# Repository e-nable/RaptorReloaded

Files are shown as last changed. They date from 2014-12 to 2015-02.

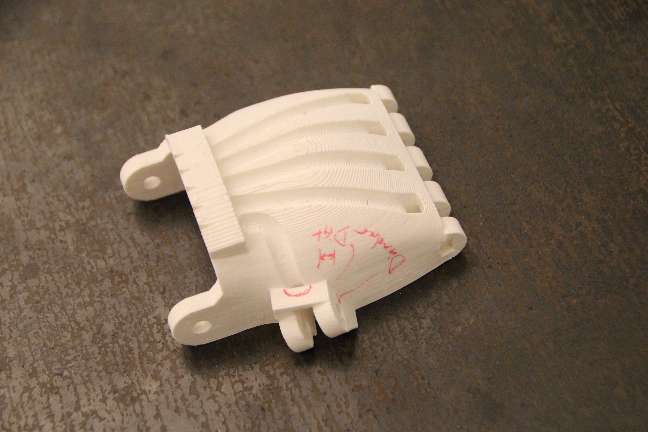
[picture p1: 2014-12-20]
Assembly Images/IMG_4811.JPG

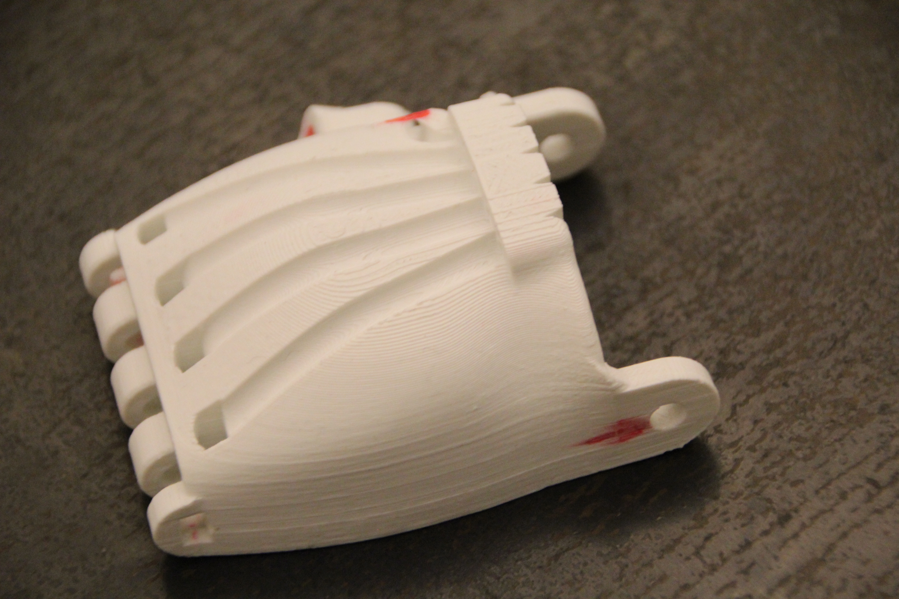
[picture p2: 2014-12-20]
Assembly Images/IMG_4816.JPG

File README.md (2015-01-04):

RaptorReloaded
==============

The Raptor Reloaded is an assistive device synthesized from designs and feedback from the e-NABLE community.  The philosophy and motivation behind this design is to lower the barrier to contribution and collaboration.  By making source files available in a variety of established and standard formats, we are making it easier for community members to test ideas using the modular and well-documented Raptor Reloaded design.  

The files in this repo are the static release files and will be updated periodically to incorporate improvements generated by the community.

## 12-20-14 Commit by AB

- added STLs oriented for use ing Hand-o-matic and plaed for printing
- aded PDF schematics of individual parts
- added images of assembly and comparisons between Raptor Reloaded, the Raptor Original, and the Cyborg Beast

## 1-4-15 Commit by AB

- fixed fit problem with finger pin (raptor_2.0_finger_pin.stl)
- updated all instances of the finger pin (HOM, Print, plates, STLs for printing.zip)

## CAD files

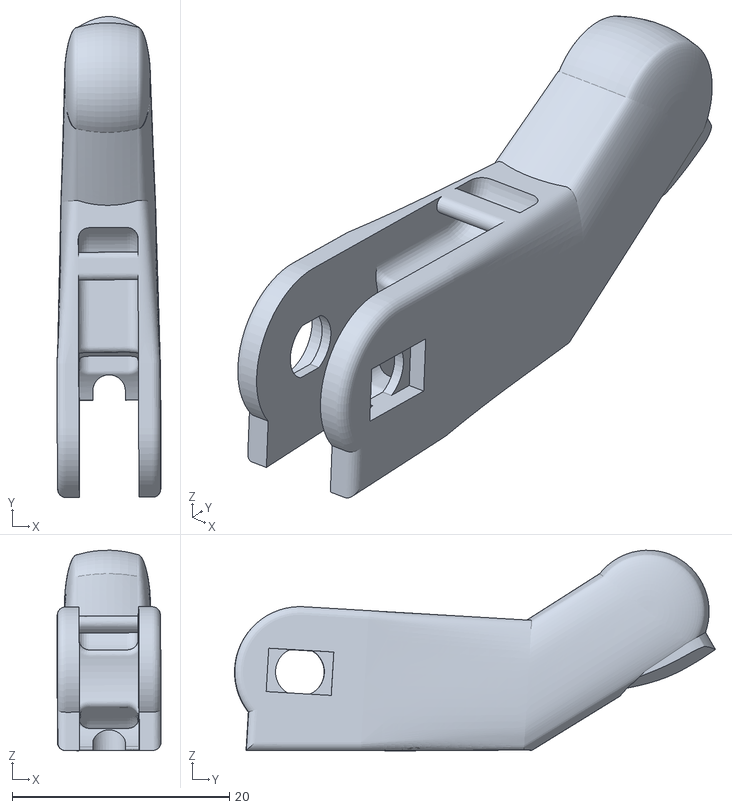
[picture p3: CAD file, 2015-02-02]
STLs/HOM/raptor_reloaded_fingertip_with_nail.stl
9.58 x 44.3 x 18.5

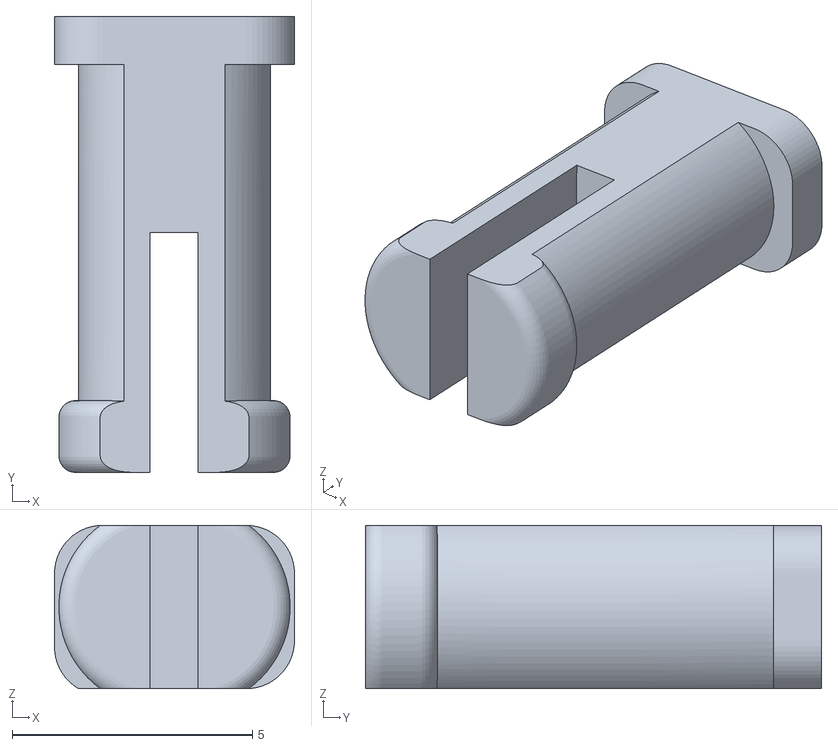
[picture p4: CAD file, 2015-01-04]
STLs/HOM/raptor_2.0_finger_pin.stl
5.00 x 9.50 x 3.40

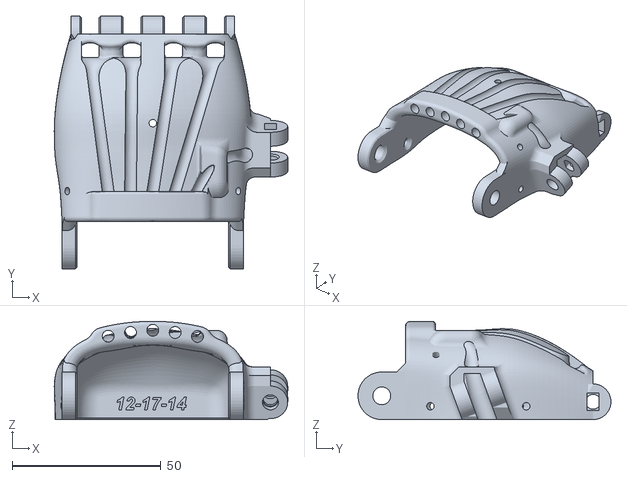
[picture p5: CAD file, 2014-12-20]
STLs/HOM/raptor_reloaded_left_palm.stl
78.4 x 85.0 x 33.0

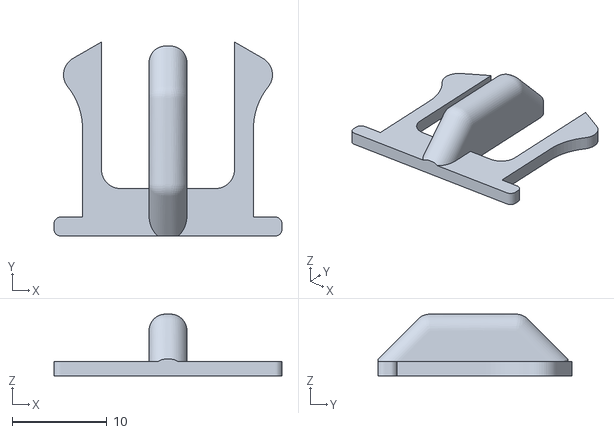
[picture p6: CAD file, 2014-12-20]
STLs/Print/raptor_reloaded_retention_clip.stl
24.0 x 20.4 x 6.50

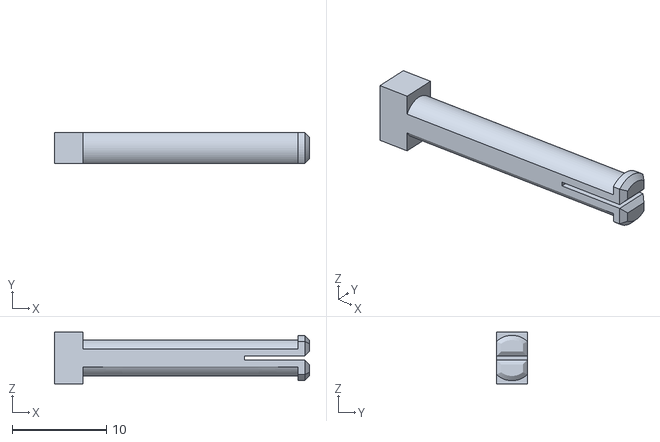
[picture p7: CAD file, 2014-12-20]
STLs/HOM/raptor_reloaded_knuckle_pin.stl
27.0 x 3.30 x 5.50

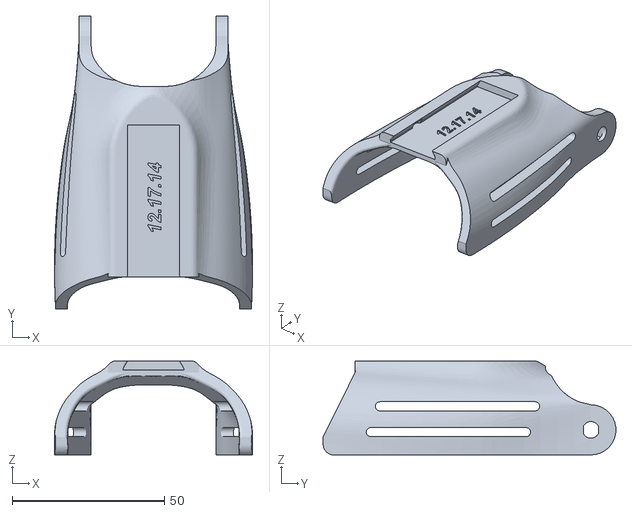
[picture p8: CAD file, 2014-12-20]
STLs/Print/raptor_reloaded_gauntlet.stl
65.1 x 96.2 x 30.9

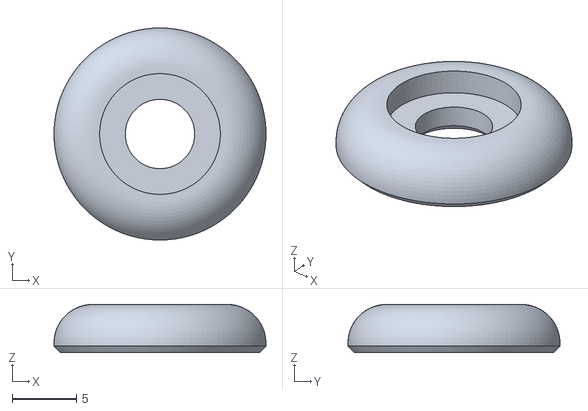
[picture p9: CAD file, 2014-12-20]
STLs/Print/raptor_reloaded_wrist_pin_cap.stl
16.5 x 16.5 x 3.75

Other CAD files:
STLs/Print/raptor_reloaded_fingertip_with_nail.stl
STLs/HOM/raptor_2.0_fingertip.stl
STLs/Print/raptor_2.0_fingertip.stl
STLs/HOM/raptor_reloaded_gauntlet.stl
STLs/Print/raptor_reloaded_knuckle_pin.stl
STLs/HOM/raptor_reloaded_gauntlet_support.stl
STLs/HOM/raptor_reloaded_left_palm_support.stl
STLs/HOM/raptor_reloaded_retention_clip.stl
STLs/HOM/raptor_reloaded_right_palm.stl
STLs/HOM/raptor_reloaded_right_palm_support.stl
STLs/HOM/raptor_reloaded_wrist_pin_cap.stl
STLs/Print/raptor_reloaded_gauntlet_supported.stl
STLs/Print/raptor_reloaded_left_palm.stl
STLs/Print/raptor_reloaded_right_palm.stl

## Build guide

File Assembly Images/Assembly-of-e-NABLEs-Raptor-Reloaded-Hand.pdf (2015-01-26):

http://www.instructables.com/id/Assembly-of-e-NABLEs-Raptor-Reloaded-Hand/

Food (http://www.instructables.com/tag/type-id/category-food/) Living (http://www.instructables.com/tag/type-id/category-living/) Outside (http://www.instructables.com/tag/type-id/category-outside/) | Play (http://www.instructables.com/tag/type-id/category-play/) | Technology (http://www.instructables.com/tag/type-id/category-technology/) Workshop (http://www.instructables.com/tag/type-id/category-workshop/)

# Assembly of e-NABLE's Raptor Reloaded Hand

by andreasbastian (http://www.instructables.com/member/andreasbastian/?utm_source=pdf&utm_campaign=title) on January 15, 2015

Table of Contents

Author:andreasbastian Andreas Bastian (http://andreasbastian.com)
Engineer and artist working with 3D printing, laser cutting, and clay.

## Intro: Assembly of e-NABLE's Raptor Reloaded Hand

The Raptor Reloaded is an updated release of the original that incorporates feedback from the e-NABLE community (https://plus.google.com/communities/102497715636887179986/) and has CAD design source files available in STEP, IGES, IPT, and F3D formats.

Updates in the 12-17-14 release include:
Improved print-ability due to custom modeled supports
Cyborg Beast compatible sizing
Improved dovetail geometry
New tensioner retention clip
Easier to use tensioner pins
Low profile elastics with two tie-off options
More access to elastic and flexsor routing channels Debossed versioning information on palm and gauntlet Slimmer, more anthropomorhpic fingers
Narrower knuckle block
More intuitive assembly (new one-way proximals)
Thorough documentation and modular design
Source files in native Fusion 360 format, also STEP and IGES
Additional velcro-mounting options as well as traditional velcro loop and leather options Re-oriented snap-pin head recesses to improve printability
Knuckle pins are now removable, making the hand easy to repair and upgrade Strengthened tie-bars on finger tips

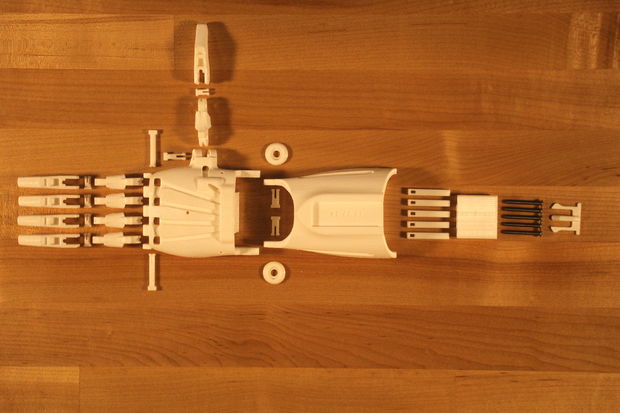
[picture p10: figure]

Image Notes
1. Palm (left)

Image Notes
1. Gauntlet

Image Notes
1. Proximal phalange

Image Notes
1. Fingertip

Image Notes
1. Finger snap pin

Image Notes
1. Knuckle snap pin

Image Notes
1. Thumb snap pin

Image Notes
1. Tensioner retention clip

Image Notes
1. Tensioner block

Image Notes
1. Tensioner pin

Image Notes
1. Wrist snap pin

Image Notes
1. Wrist snap pin cap

## Step 1: Size and Print the Parts, Secure Hardware

Download the latest Raptor Reloaded parts form Thingiverse. (http://www.thingiverse.com/thing:596966) The files are ready to print as is and do not require additional support material as custom removable support structures have already been modeled into the palm and gauntlet files. If you do wish to print without the included support, files without support are also available on the Thingiverse page.

There are two main options for sizing the Raptor Reloaded:

Linear Scaling (easy)

The main measurement used in sizing the Raptor Reloaded is the width of the recipient's complete hand at the knuckles. At 100% scale, the palm of the Raptor Reloaded measures 55mm at its widest point. To get the appropriate linear scaling factor for scaling the STLs, add 5mm (to account for the thickness of padding in the printed palm) to the width of the recipient's complete hand at its widest point. Divide this number by 55 to get the scaling factor for the STLs. For example, if the palm is 65mm wide, then 65 + 5 = 70, and 70 / 55 = 1.27, so the scaling multiplier would be 1.27 or 127%. Make sure to apply the scaling factor to all of the parts to ensure that they fit together. At higher scales, the clearances between the moving parts of the hand will grow, so glue or other modifications may be necessary to ensure that all the pieces stay secured to each other.

Parametric (more involved):

Because radial and lateral clearances for motion assemblies are absolute, linear scaling can cause problems at large scales. For those with some CAD experience, the native Fusion 360 source files as well as STEP and IGES files are available here. (http://a360.co/1uV2X0G) Detailed technical drawings can be found on the github. (https://github.com/e-nable/RaptorReloaded/tree/master/Drawings) For an introduction to modeling in Fusion 360, see the Getting Started in Fusion 360 (http://enablingthefuture.org/resources/getting-started-in-fusion-360/) page on enablingthefuture.org.

Recommended Printing Settings:
PLA (or ABS, PET, Nylon)
0.2mm layers
2 shells
35% infill
Active cooling fan on

Additional Materials:

The Raptor Reloaded requires some additional hardware to assemble, most of which can be sourced from the Hardware Sources (http://enablingthefuture.org/resources/hardware-sources/) page on the e-NABLE website. 4ft Velcro, double-sided (2” wide) (http://www.amazon.com/Velcro-Nylon-Length-Width-Black/dp/B003L1W4DQ/ref=pd_sim_op_5)

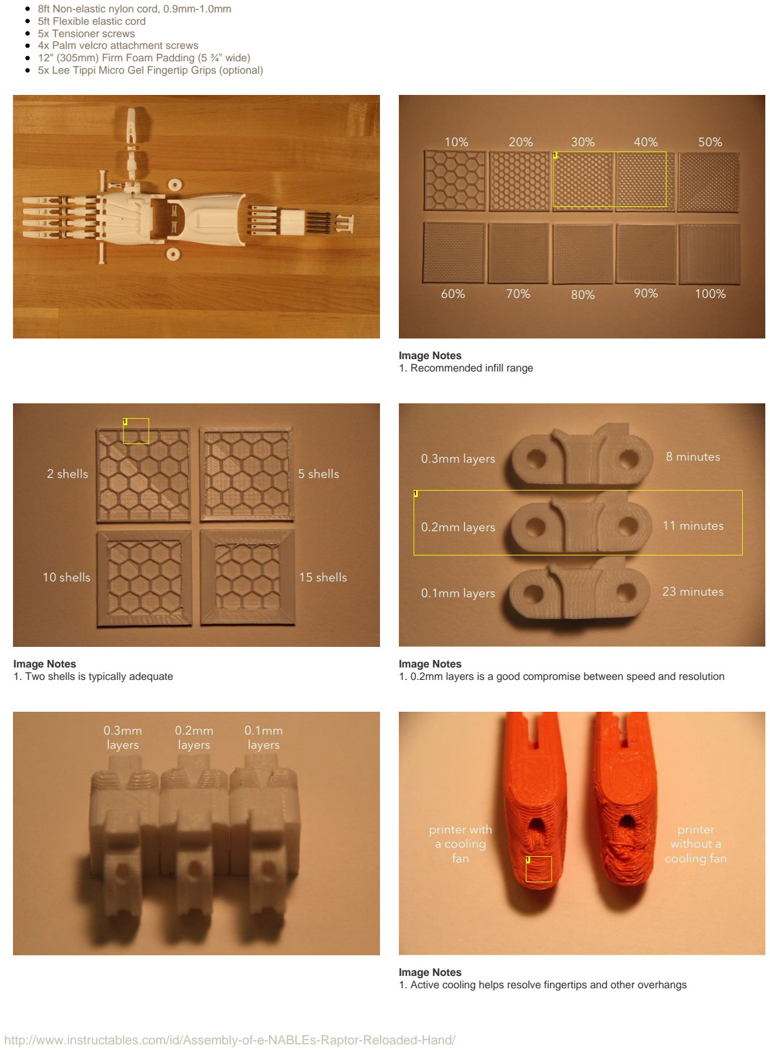
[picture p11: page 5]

8ft Non-elastic nylon cord, 0.9mm-1.0mm (http://www.amazon.com/gp/product/B009661Y72/) 5ft Flexible elastic cord (http://www.amazon.com/gp/product/B0047BIRUS/)
5x Tensioner screws (https://www.boltdepot.com/Socket_button_head_Stainless_steel_18-8.aspx)
4x Palm velcro attachment screws (https://www.boltdepot.com/Socket_flat_head_Stainless_steel_18-8.aspx)
12" (305mm) Firm Foam Padding (5 ¾” wide) (http://www.pattersonmedical.com/app.aspx?cmd=getProductDetail&key=070_921018416) 5x Lee Tippi Micro Gel Fingertip Grips (optional) (http://www.amazon.com/s/ref=nb_sb_noss_2?url=search-alias%3Daps&field-keywords=gel+tippi)

Image Notes
1. Recommended infill range

Image Notes
1. Two shells is typically adequate

Image Notes
1. 0.2mm layers is a good compromise between speed and resolution

Image Notes
1. Active cooling helps resolve fingertips and other overhangs

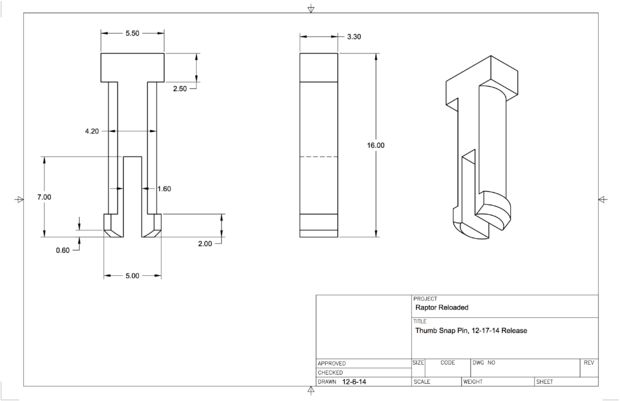
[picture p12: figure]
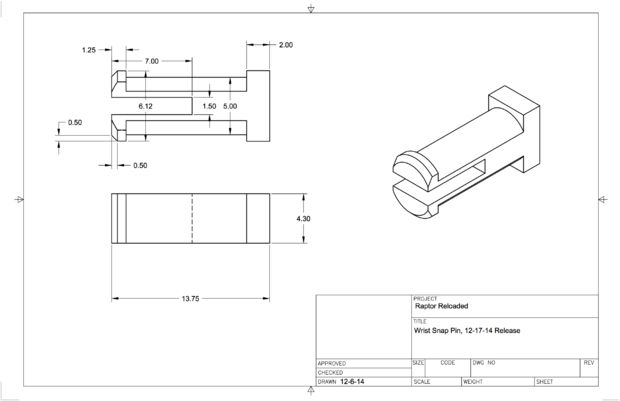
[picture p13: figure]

## Step 2: Assemble the Palm and Fingers

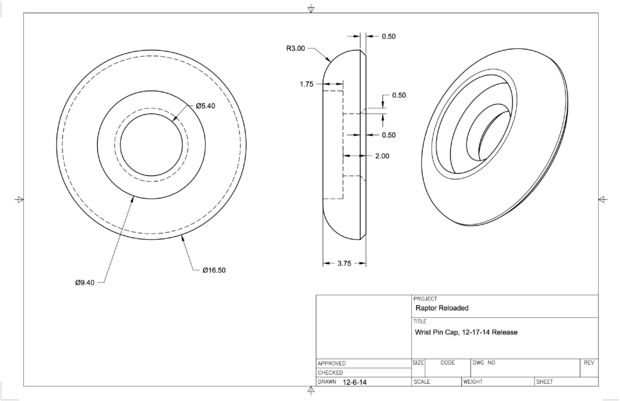
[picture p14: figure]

Start by removing the support structure, which can be done by inserting any edged tool in between the palm and the support structure and twisting. Next, check the fingertips for any defects. Small pieces of filament sometimes droop in the rectangular recess for the snap pin head-- be sure to remove these to ensure the snap pin seats well.

Assemble the fingers by inserting the proximal phalange into the matching recess in the fingertip, making sure the raised hard stop (the "square" region on top of one side of the proximal phalange) is facing away from the fingertip and the two small ridges on the top of the proximal meet the matching "wings" of the fingertip. Insert the snap pin and press until the rectangular head is seated in it's recess and the other end of the pin is flush with the sides of the fingertip. Repeat for the remaining four fingers. Attach the one finger to the thumb knuckle on the palm using the thumb pin and attach the other four fingers in the knuckles using the two knuckle pins. It is often helpful to get the knuckle pin started and then push its head using a table. If at a later point you need to remove or replace fingers, the knuckle pins can be backed out by pressing on their tips using the slot in between the bases of the middle and ring finger.

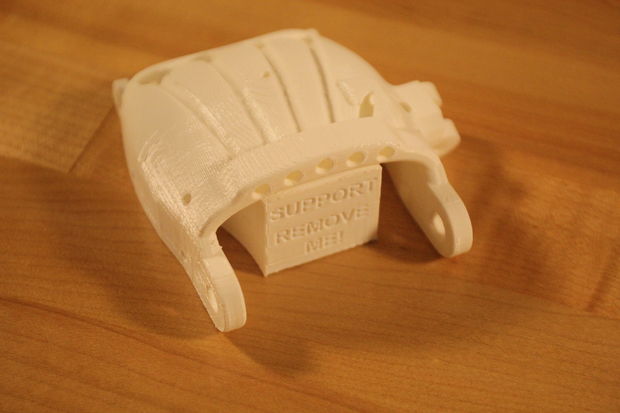
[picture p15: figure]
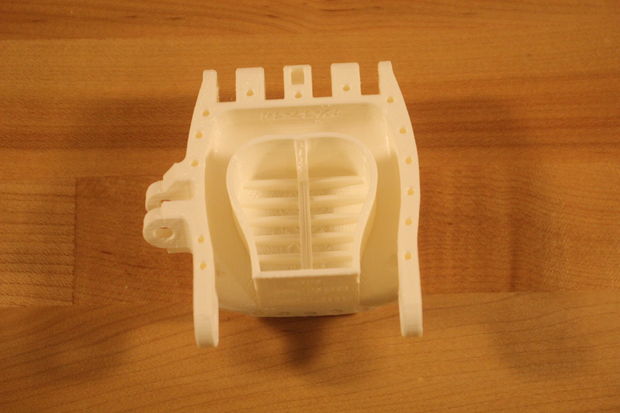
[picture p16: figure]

Image Notes
1. Any tool with an edge will work for removing the support structure.

Image Notes
1. Sometimes the fingertips print with a small defect here.

Image Notes
1. It can be removed with a blade or tweezers.

Image Notes
1. Fingertip

Image Notes
1. Thumb pin

Image Notes
1. The knuckle snap pins can be removed by pushing on them from this slot.

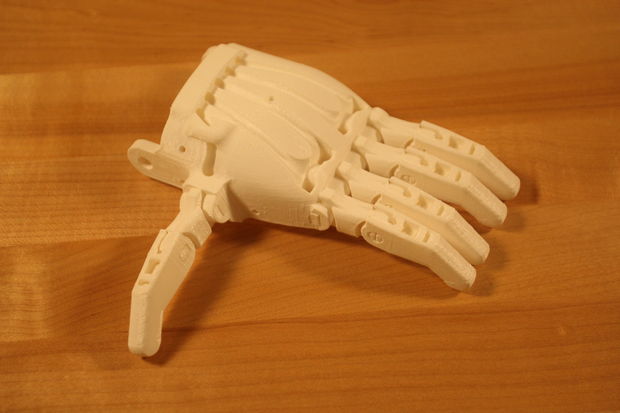
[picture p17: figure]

## Step 3: Install the Elastics in the Fingers

Check the Hardware Sources (http://enablingthefuture.org/resources/hardware-sources/) page on the e-NABLE website for vetted elastics options. I used 1.0mm black Beadlon elastic fabric cord (http://beadalon%20fabric%20elastic/) from Amazon. Cut five lengths each a little longer than two finger lengths. I like to use tweezers to navigate the tight spaces where the elastics are tied. The goal of the elastics is to just counter to force of gravity on the fingers and to hold them gently open. This opening force is calibrated when tying the second end of the elastic cord to the back of the palm. The fingers should snap up after being pressed down, but should not require significant force to close.

Sarting with the thumb, thread one end of a length of elastic cord under the bar on the back of the thumb tip until there is a little over an inch (30-35mm) of cord on the other side of the bar. Tie a clinch knot by twisting the free end around the longer side 2-4 times, then thread the free end through the loop at the base of the twist and through again the resulting loop:

After threading the elastic cord through the proximal and up through the cable guide, use the clinch (or two half hitch) knot to secure the end of the elastic cord to the cable guard as shown in the pictures. The goal is to use this knot to set the tension on the thumb, so tie it carefully after getting the appropriate tension.

For the remaining four fingers, I like to use the clinch knot on the finger tips and a two half hitch knot to secure the other end of each elastic to the rear cable guide on the palm. The two half hitch knot allows you to control the tension while tying the knot. See below:

Finally, I like to finish each elastic knot with super glue to ensure that it won't slip. Additional half hitchs can be used as well.

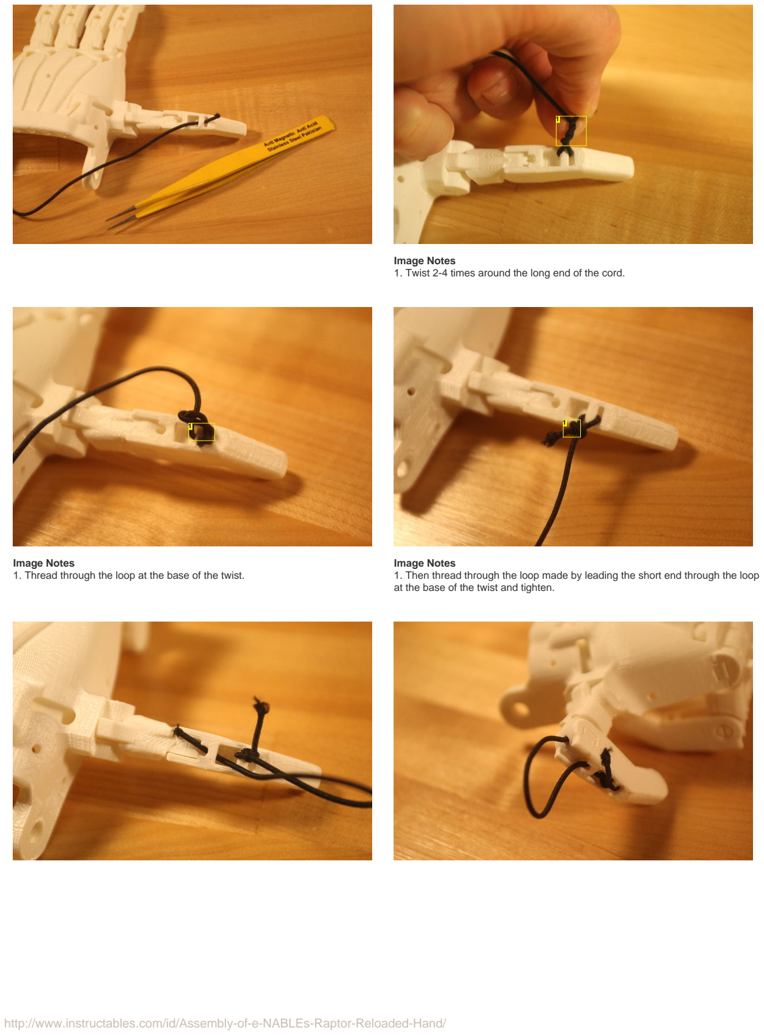
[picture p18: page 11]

Image Notes
1. Twist 2-4 times around the long end of the cord.

Image Notes
1. Thread through the loop at the base of the twist.

Image Notes
1. Then thread through the loop made by leading the short end through the loop at the base of the twist and tighten.

Image Notes
1. I used a clinch knot again, but a two half hitch would work just as well if not better.

Image Notes
1. Trim the knot tails.

Image Notes
1. A drop of superglue helps secure each knot.

Image Notes
1. One half hitch.

Image Notes
1. Adjust the tension using the single half hitch, then tie a second half hitch to lock it in.

Image Notes
1. Two half hitch knot keeps the cord from slipping.

Image Notes
1. Two half hitches.

## Step 4: Install the Flexsors in the Fingers

Again, check the Hardware Sources (http://enablingthefuture.org/resources/hardware-sources/) page on the e-NABLE website for other vetted sources of flexsor line. This braided nylon fishing line (http://www.amazon.com/gp/product/B009661Y72/) is the current recommended material for the flexsors. As with the elastic lines, I like to use a clinch knot to secure the flexsors to the finger tips.

Cut five lengths of nylon line, each as long as the ultimate length of the assembled hand (fingers plus palm plus gauntlet). This is a good way to make sure that you have enough line when working with different scales. Starting with the thumb, use a clinch knot to tie on e end of the flexsor line to the tie-bar. Then thread the line through the proximal and up through the proximal knuckle where the proximal phalange meets the palm. Be careful to ensure that the line doesn't get wrapped around the elastic cord for each finger. It should run parallel to it up over the top of the palm and out the back of the rear cable guide. Repeat this process for the other four fingers. After trimming the knot tails, I like to singe the tail to prevent fraying and then apply a drop of superglue to make sure the knot doesn't slip.

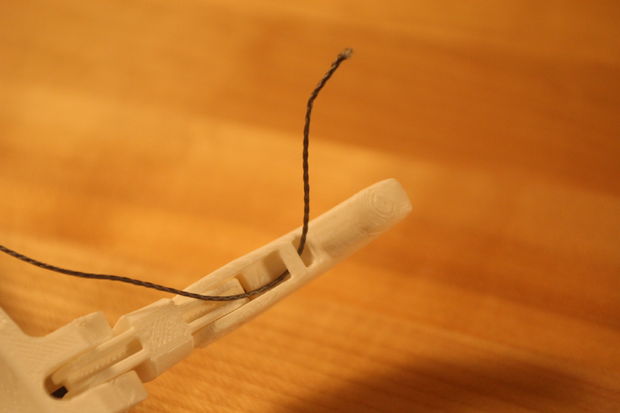
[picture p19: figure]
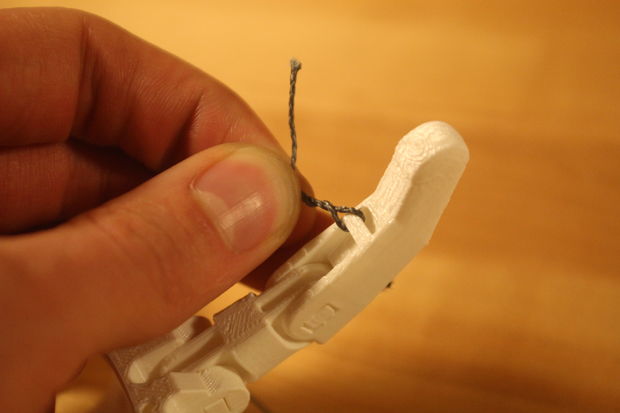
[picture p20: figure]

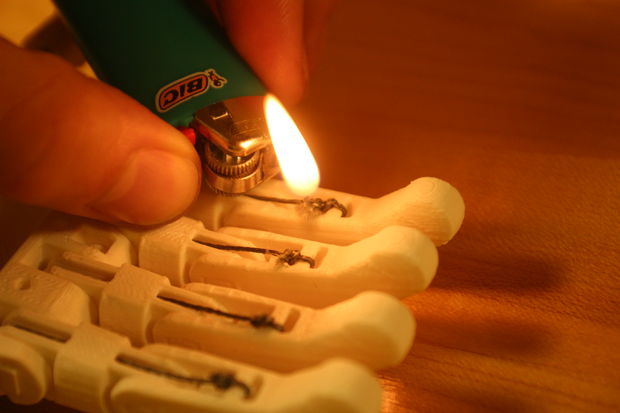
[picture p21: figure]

## Step 5: Attach the Palm to the Gauntlet

Using an edged tool, remove the gauntlet support structure and set it asides for use in the next step. Press the two wrist snap pins through the holes in the gauntlet, making sure they are aligned with the head recesses on the inner faces of the gauntlet. Once they have snapped through, back the tips back and slide the palm into position so that the wrist axis is aligned. Press the wrist pins through the palm's wrist holes. If necessary, the wrist can be bent back and the corner of a table can be used to apply pressure to the pins. Once the pins are properly seated, snap the pin caps over each pin to complete the wrist.

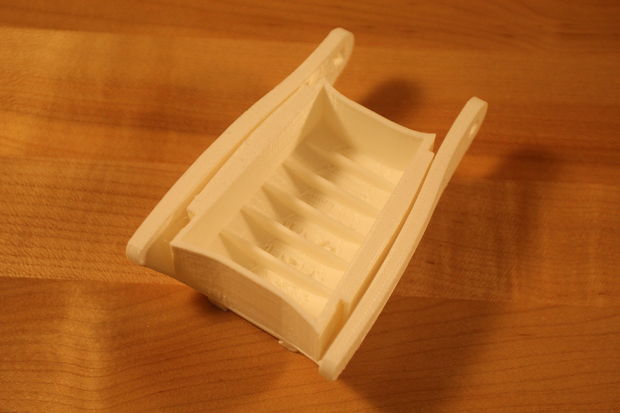
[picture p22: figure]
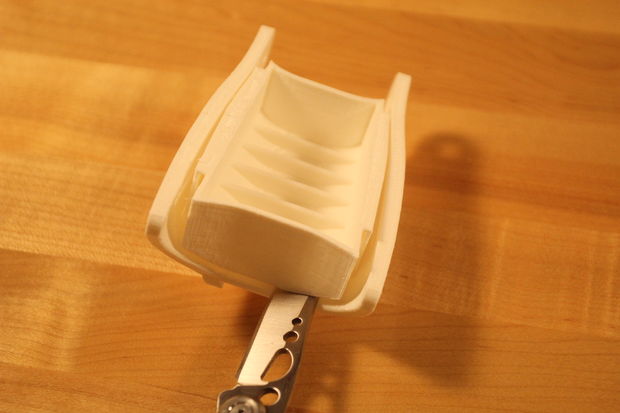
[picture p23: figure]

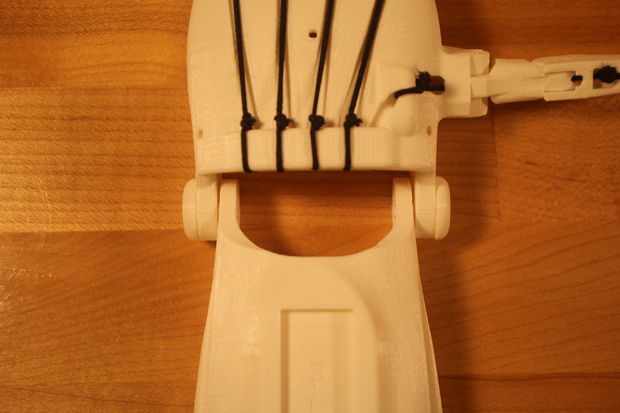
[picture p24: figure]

## Step 6: Install the Tensioner

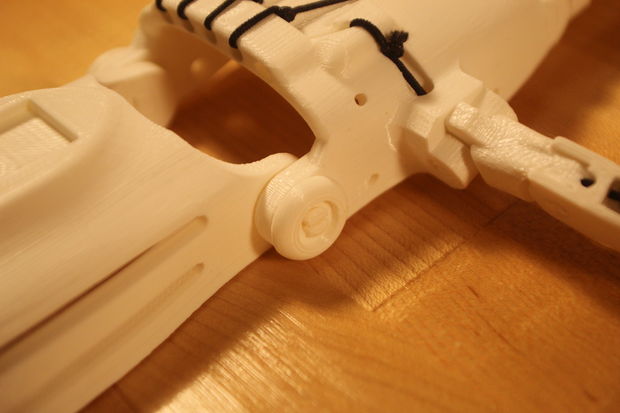
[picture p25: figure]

The tensioner is part of the design that suffers from linear scaling in that the holes in the tensioner pins change size as they are scaled for different recipients, so they will require different screws at different scalings. At 100% scale, the tensioner pins are sized to receive M3 screws. If you have access to a tap, it makes threading the tensioner pins easier, but it is optional.

Start by threading the tensioner pins, either with a tap or with the screw that will be paired with it. If using the screws to form the threads, first insert the tensioner pins into the tensioner block with the holes in the end of the pin facing "up". This will leave more room for knot tying later. Screw the screws about half-way in so that the tensioner pins can slide forward and backward in the tensioner body. Slot the body into the dovetail on the gauntlet and place the gauntlet support under the fingers of the hand to tilt the palm backwards slightly. Push all but the thumb tensioner pin back leaving just the thumn tensioner pin forward. Maintaining tension on the line, tie the thumb line to the pin using a cow hitch (see below) followed by a half hitch running through the cow hitch and a second half hitch around the flexsor line (see pictures). Because the wrist is bent back and the tensioner pins are half-tightened, the tensioner screws can be backed out or tightened in to adjust the tension on the flexsor lines. Repeat the process for the remaining fingers, trim the lines, singe the tails, and apply a drop of superglue.

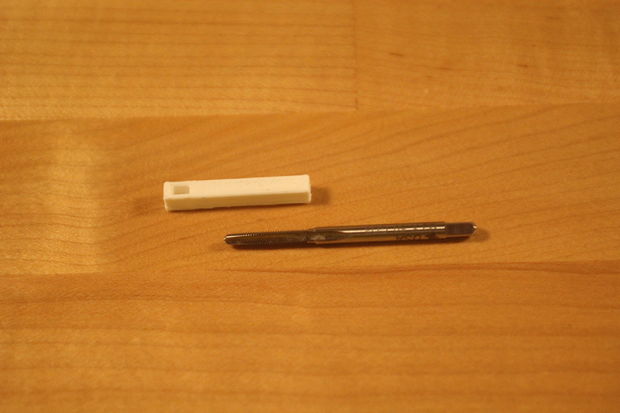
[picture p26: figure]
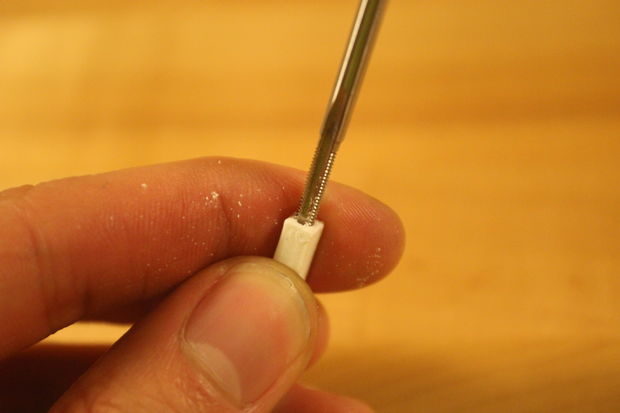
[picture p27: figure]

Image Notes
1. Be careful that the pins are aligned with the holes facing up.
2. Be careful to assemble with the holes facing up.

Image Notes
1. Gauntlet support structure

Image Notes
1. Draw the line up from below through the slot in the pin.

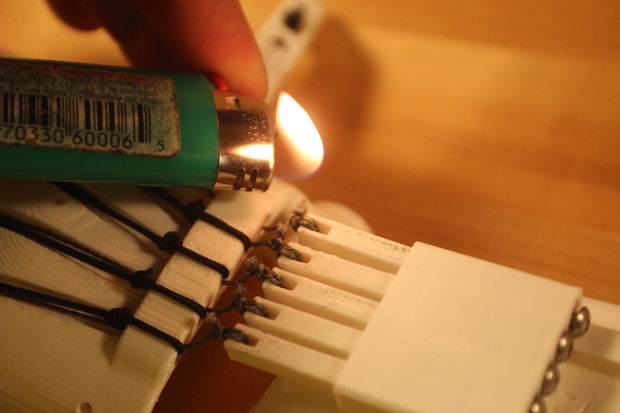
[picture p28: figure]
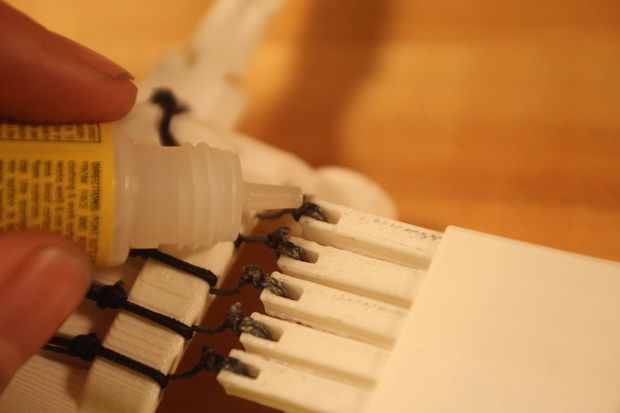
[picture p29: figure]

## Step 7: Palm Options: Padding and Velcro, Leather, or Thermomesh

Now that the mechanics of the hand are complete, it's time to prepare if to use by a recipient by applying medical grade foam padding and velcro straps. I purchased my foam from Patterson Medical, (http://www.pattersonmedical.com/app.aspx?cmd=getProductDetail&key=070_921018416) one of the suppliers from the Hardware Sources (http://enablingthefuture.org/resources/hardware-sources/) page. Cover the interior surfaces of the palm with adhesive-back foam cut to size and save extra foam for fine-tuning the fit based on recipient feedback.

There are several options for enclosing the palm:
Single velcro strap
Double velcro strap
Riveted leather
Thermomesh (integrated or attached)

In this example hand, I used the single velcro strap as it has less give than the two strap option. Again, if you have a tap, it is nice to tap the four holes on the sides of the palm for securing the velcro, but it is not necessary. Cut a strip of soft-sided velcro to be 1/2" (~12mm) longer than the palm is wide on either side. Fold each side down and use the tips of tweezers or an awl through the mounting holes to mark the hole locations on the velcro. Use flat head stainless steel fasteners to secure the velcro to the inside of the palm. Repeat on the other side of the palm. It is helpful to have a ball-headed allen key to turn the screws closest to the knuckles.

Leather can also be cut to match the profile of the palm and screws can be driven into the holes around the perimeter to secure it.

Thermomesh palms, both integrated and bolt-on, have been successfully tested in the e-NABLE and will soon be available for more wide use.

Image Notes
1. The two-strap method.

Image Notes
1. For the single strap method, use a 1/2" (12mm) overhand on each side

Image Notes
1. Punch through the velcro with something sharp (tweezers in this case).

Image Notes
1. Widen the hole so that a screw can pass through.

Image Notes
1. Flat head stainless steel fastener.
2. Punching the second hole.

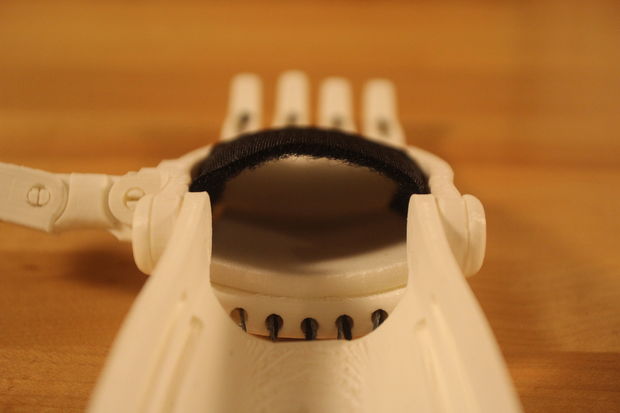
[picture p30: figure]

## Step 8: Install Padding and Straps on the Gauntlet

Using the same foam as for the palm, cut a section to roughly match the inner surface of the gauntlet. I find it easiest to remove the gauntlet from the palm for this part or to do it before the tensioner. With better access to the gauntlet, a pen can be used to trace the edge of the gauntlet onto the foam for a clean fit.

After applying the foam, cut a strip of double sided or soft-sided velcro to be slightly longer than the assembled hand. Slide the strap through the "bottom" (closest to the build platform during printing) slots in the gauntlet with the soft side facing the foam. Position the long end of the strap on the same side as the thumb and tuck 1.5" (38mm) of the short end through the "top" slot and fold it back to meet the long side of the strap. Then either stitch or hotglue this short end back to the long strap. Fold the long end of the strap back in on itself (towards the gauntlet) so that when folded again, it can reach the far edge of the gauntlet where the short end of the strap is. Hot glue or stitch the folded end down to the long end of the strap. If using two-sided velcro, the long end should now have the soft loops on both sides and can be tightened down and secured on the hooks of strap portion between the wings of the gauntlet. If using separate loop and hook straps, cut and hot glue or stitch a section of hook strap to the area of the strap between the two wings to that the long end of the strap can be secured there. This strapping configuration is designed to be easy to use with the other more dextrous hand.

Finally, click the tensioner retention clip into the back of the dovetail to ensure that the tensioner doesn't have any opportunities to fall out.

Image Notes
1. Mark the edge here.
2. Mark the edge here.

Image Notes
1. Once the foam is sized, attach here.

Image Notes
1. Attachment pad.
2. Fold over portion.

Image Notes
1. Hot glue or stitch.

Image Notes
1. Apply hot glue or stitches here.

Image Notes
1. Hot glue.

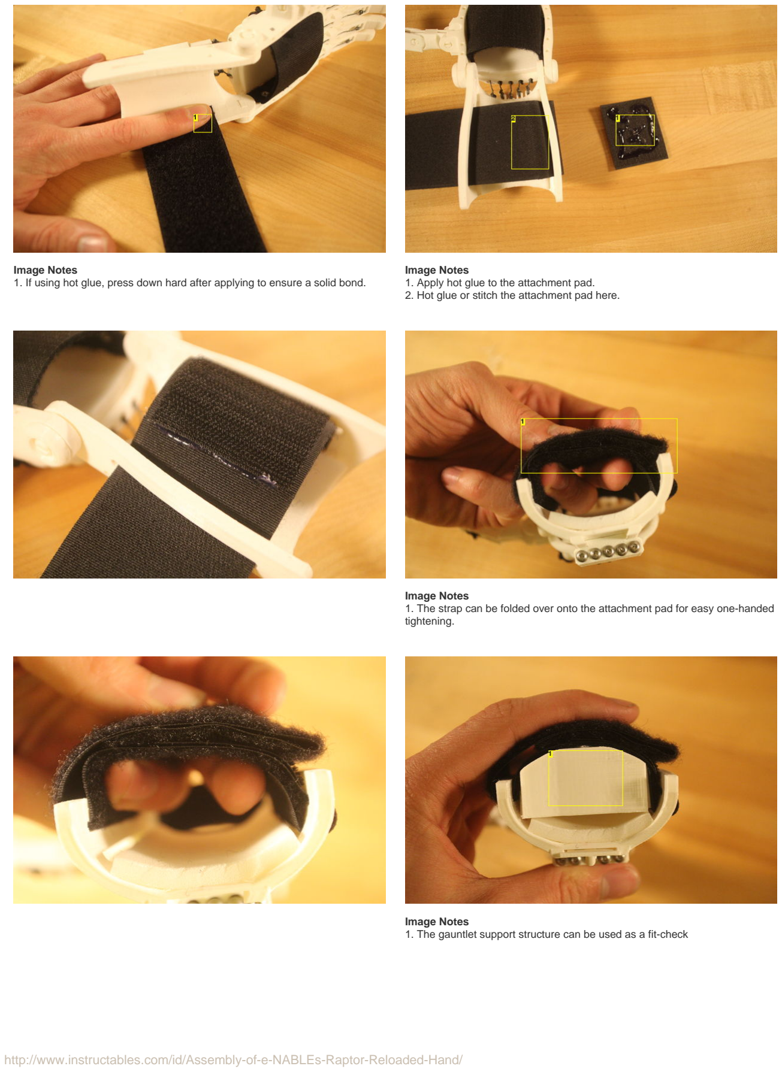
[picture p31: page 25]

Image Notes
1. If using hot glue, press down hard after applying to ensure a solid bond.

Image Notes
1. Apply hot glue to the attachment pad.
2. Hot glue or stitch the attachment pad here.

Image Notes
1. The strap can be folded over onto the attachment pad for easy one-handed tightening.

Image Notes
1. The gauntlet support structure can be used as a fit-check

Image Notes
1. Insert the tensioner retention clip to finish the hand.

## Step 9: Next Steps

Congratulations! You finished building the hand! Hopefully this is the first of many. Work with and listen to recipients' feedback about fit and comfort. We recommend using a prosthetic sock or similar sleeve when using these devices. Beeswax can be used to lubricate the joints and reduce squeaking. As the elastics break in, the flexsors may need a little tightening to maintain performance.

Share feedback with the e-NABLE research and development community in the Google Plus community (https://plus.google.com/communities/102497715636887179986/) and together we can iterate upon and improve the design!

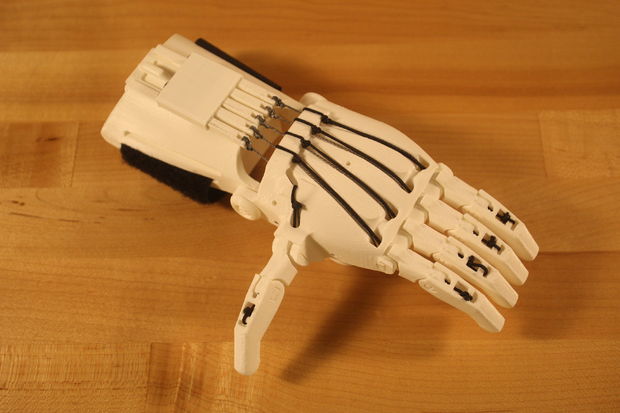
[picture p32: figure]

## Related Instructables

Thermoforming
3D Printed PLA
for Use in
Prostethics (http://www.instructables.com/id/Thermoforming-3D-Printed-PLA-for-Use-in-Prostethic/) by
andreasbastian (http://www.instructables.com/member/andreasbastian/?utm_source=pdf&utm_campaign=related)

Sugru
Overmolding
Using 3D
Printed Molds (http://www.instructables.com/id/Sugru-Overmolding-Using-3D-Printed-Molds/)
by
andreasbastian (http://www.instructables.com/member/andreasbastian/?utm_source=pdf&utm_campaign=related)

Techniques for
3D printing in
Nylon (http://www.instructables.com/id/Techniques-for-3D-printing-in-Nylon/) by
Branebot (http://www.instructables.com/member/Branebot/?utm_source=pdf&utm_campaign=related)

Superhero Arm (http://www.instructables.com/id/Playful-Prosthetic-Arm/?utm_source=pdf&utm_campaign=related)
by CobyUnger (http://www.instructables.com/member/CobyUnger/?utm_source=pdf&utm_campaign=related)

Falcon Hand V1 (http://www.instructables.com/id/Falcon-Hand-V1/?utm_source=pdf&utm_campaign=related)
by B-town (http://www.instructables.com/member/B-town/?utm_source=pdf&utm_campaign=related)

Prosthetic Leg (http://www.instructables.com/id/Customizable-Prosthetic-Leg/?utm_source=pdf&utm_campaign=related)
by lhoard6 (http://www.instructables.com/member/lhoard6/?utm_source=pdf&utm_campaign=related)

Advertisements

## Comments

1 comments | Add Comment (http://www.instructables.com/id/Assembly-of-e-NABLEs-Raptor-Reloaded-Hand/)

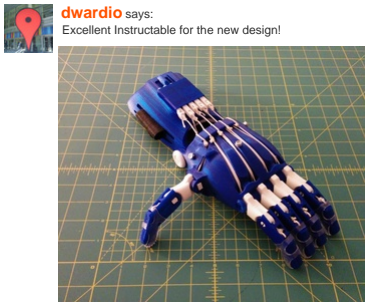
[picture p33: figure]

dwardio (http://www.instructables.com/member/dwardio/?utm_source=pdf&utm_campaign=comments) says: | Jan 19, 2015. 6:49 PM REPLY (http://www.instructables.com/id/Assembly-of-e-NABLEs-Raptor-Reloaded-Hand/)
Excellent Instructable for the new design!

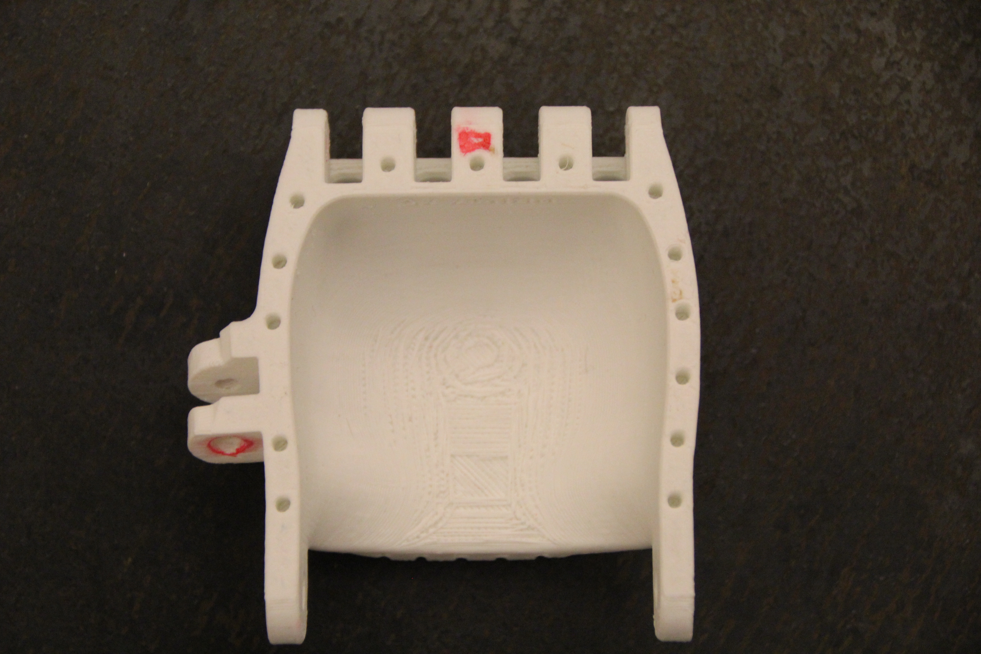
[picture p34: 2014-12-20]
Assembly Images/IMG_4814.JPG

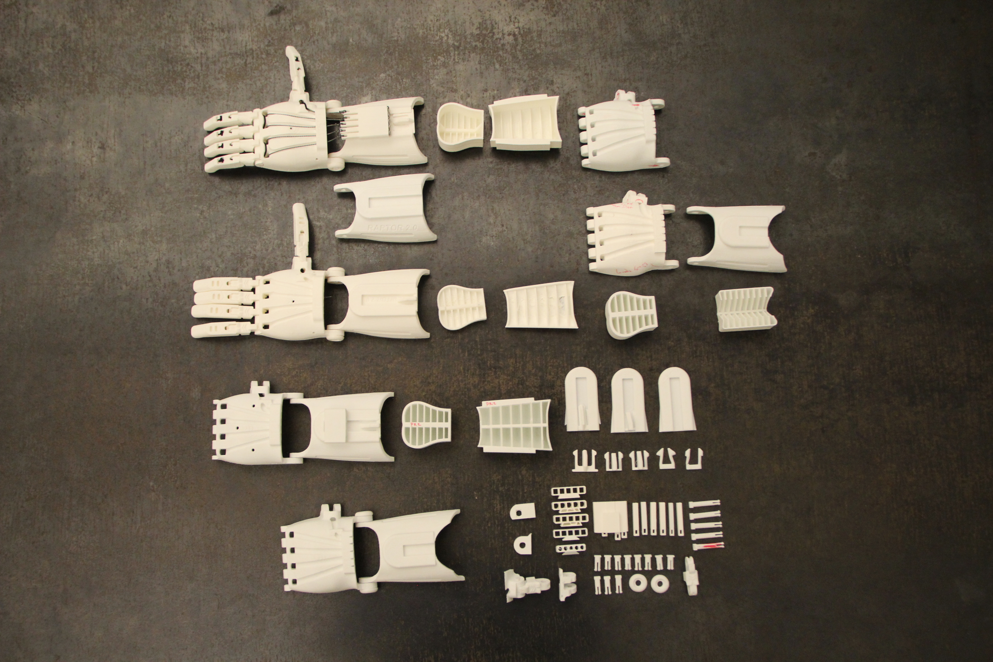
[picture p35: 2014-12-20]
Assembly Images/IMG_4797.JPG

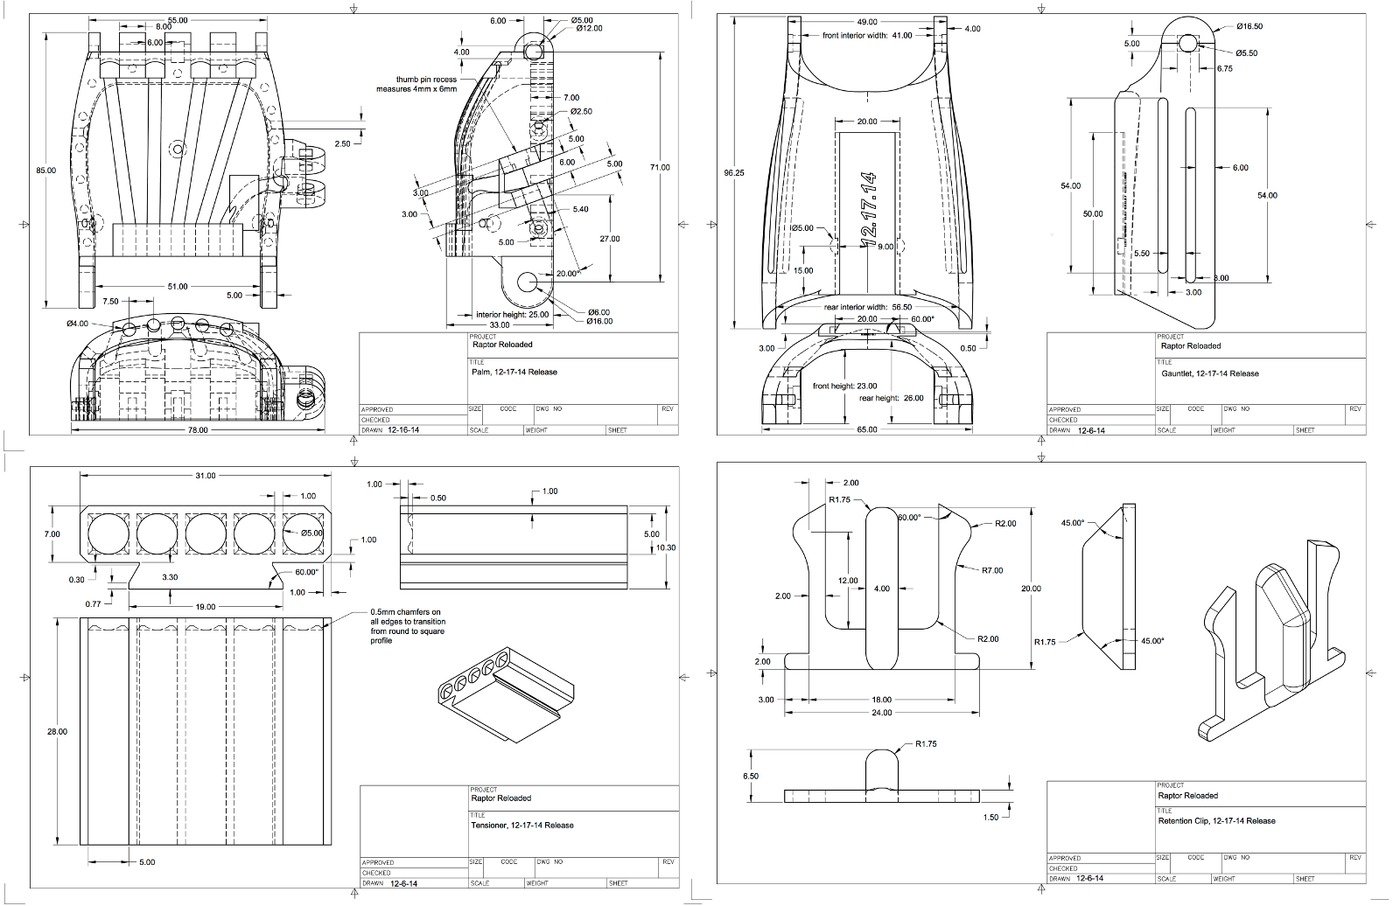
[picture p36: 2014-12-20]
Assembly Images/comparisons/primary_drawings.png

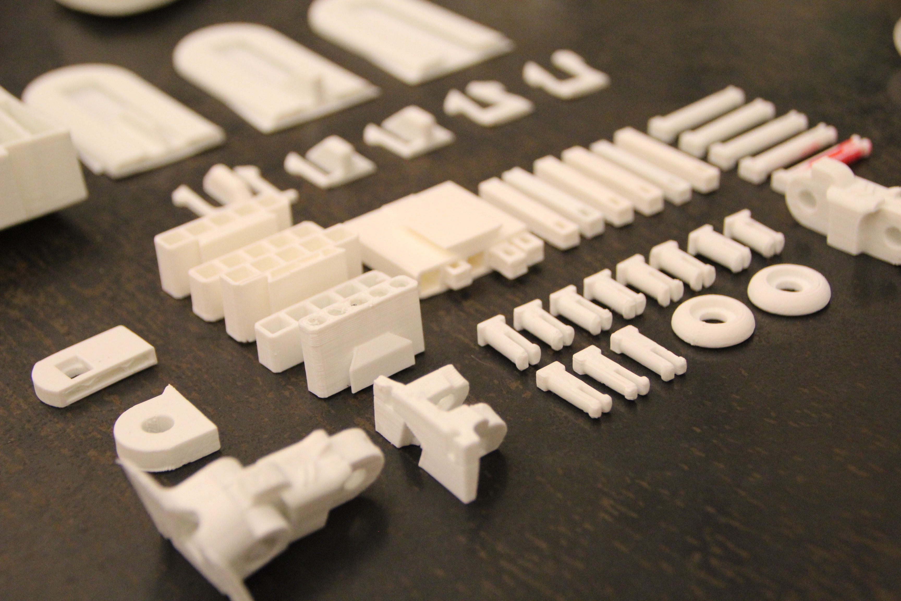
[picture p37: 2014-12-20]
Assembly Images/IMG_4838.JPG

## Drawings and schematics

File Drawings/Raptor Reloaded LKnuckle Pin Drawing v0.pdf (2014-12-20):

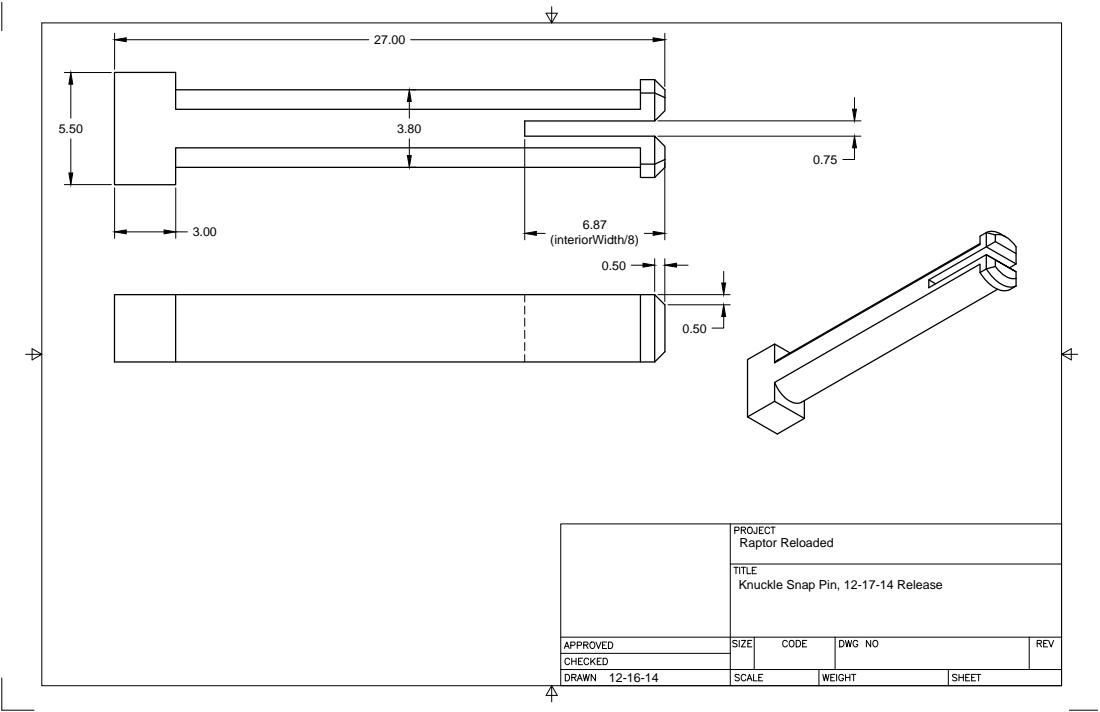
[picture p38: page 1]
Raptor Reloaded

Knuckle Snap Pin, 12-17-14 Release

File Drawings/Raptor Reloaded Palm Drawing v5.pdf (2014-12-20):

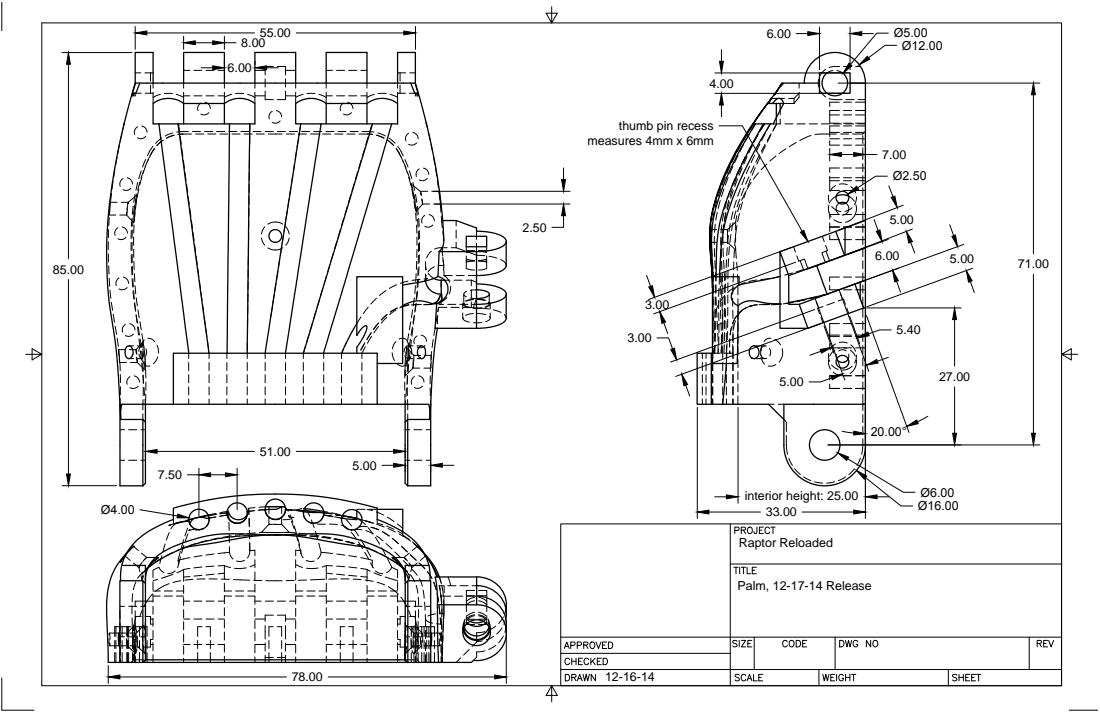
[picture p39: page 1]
Raptor Reloaded; Palm, 12-17-14 Release; interior height: 25.00

thumb pin recess
measures 4mm x 6mm

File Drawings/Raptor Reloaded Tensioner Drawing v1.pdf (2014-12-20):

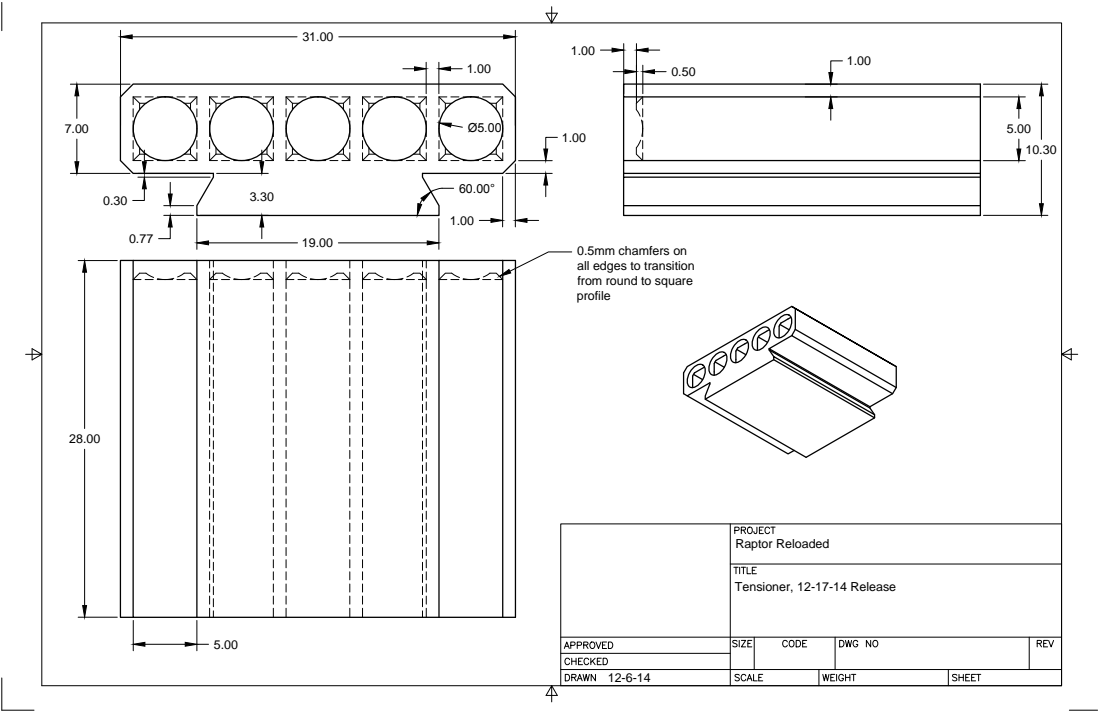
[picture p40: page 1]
Raptor Reloaded; Tensioner, 12-17-14 Release

0.5mm chamfers on
all edges to transition
from round to square
profile

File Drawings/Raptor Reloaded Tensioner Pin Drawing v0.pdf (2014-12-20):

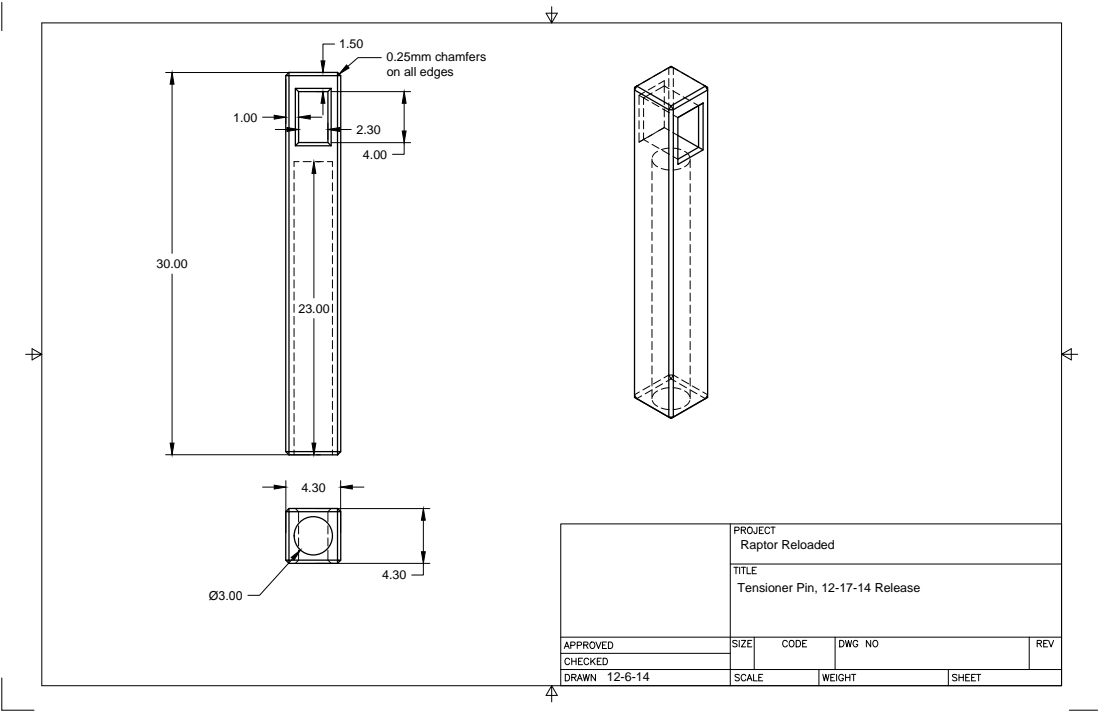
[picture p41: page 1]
Raptor Reloaded

0.25mm chamfers
on all edges

Tensioner Pin, 12-17-14 Release

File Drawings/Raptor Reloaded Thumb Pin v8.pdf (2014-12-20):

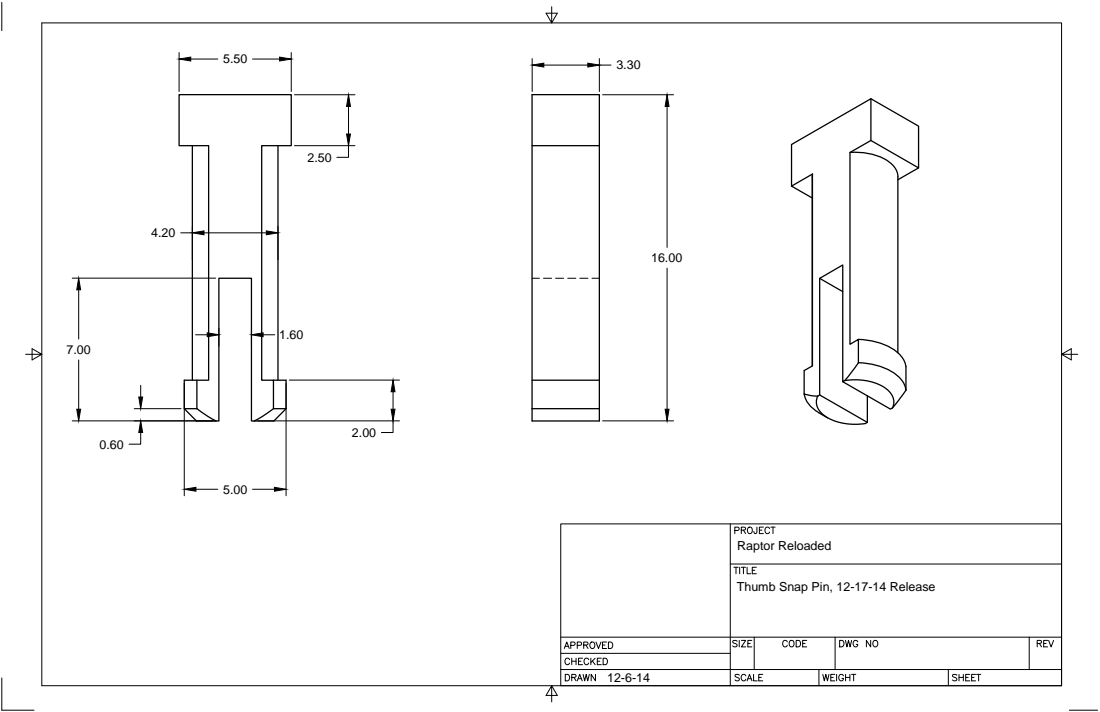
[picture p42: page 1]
Raptor Reloaded

Thumb Snap Pin, 12-17-14 Release

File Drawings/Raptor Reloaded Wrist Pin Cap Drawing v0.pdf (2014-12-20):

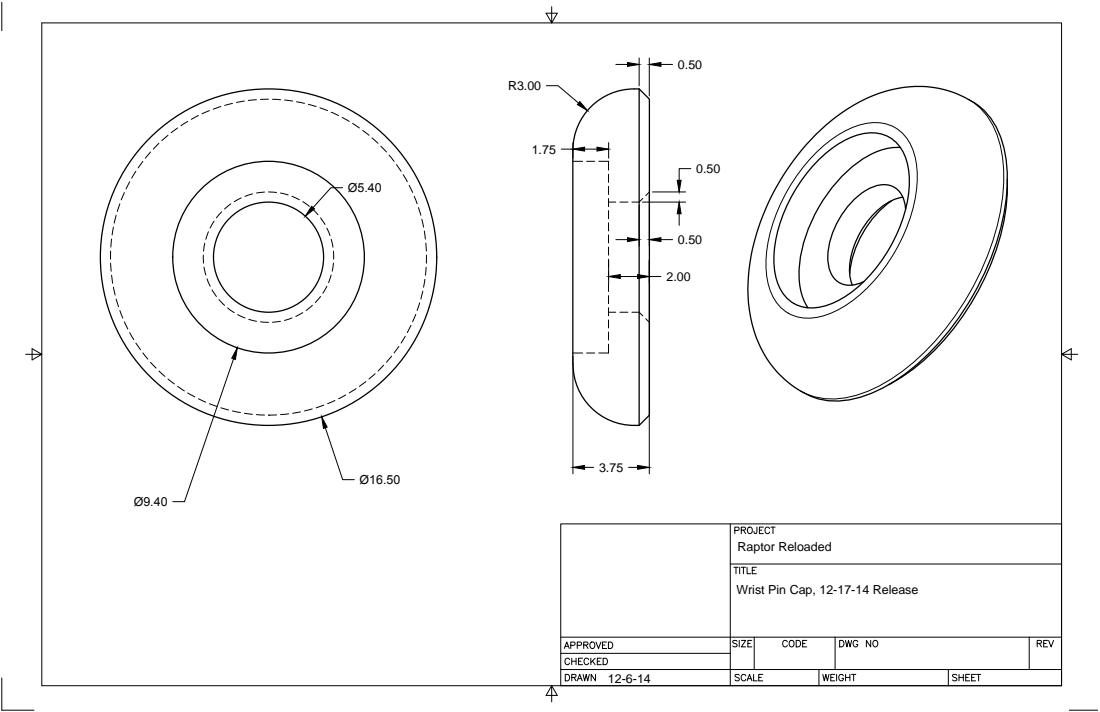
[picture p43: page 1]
Raptor Reloaded

Wrist Pin Cap, 12-17-14 Release

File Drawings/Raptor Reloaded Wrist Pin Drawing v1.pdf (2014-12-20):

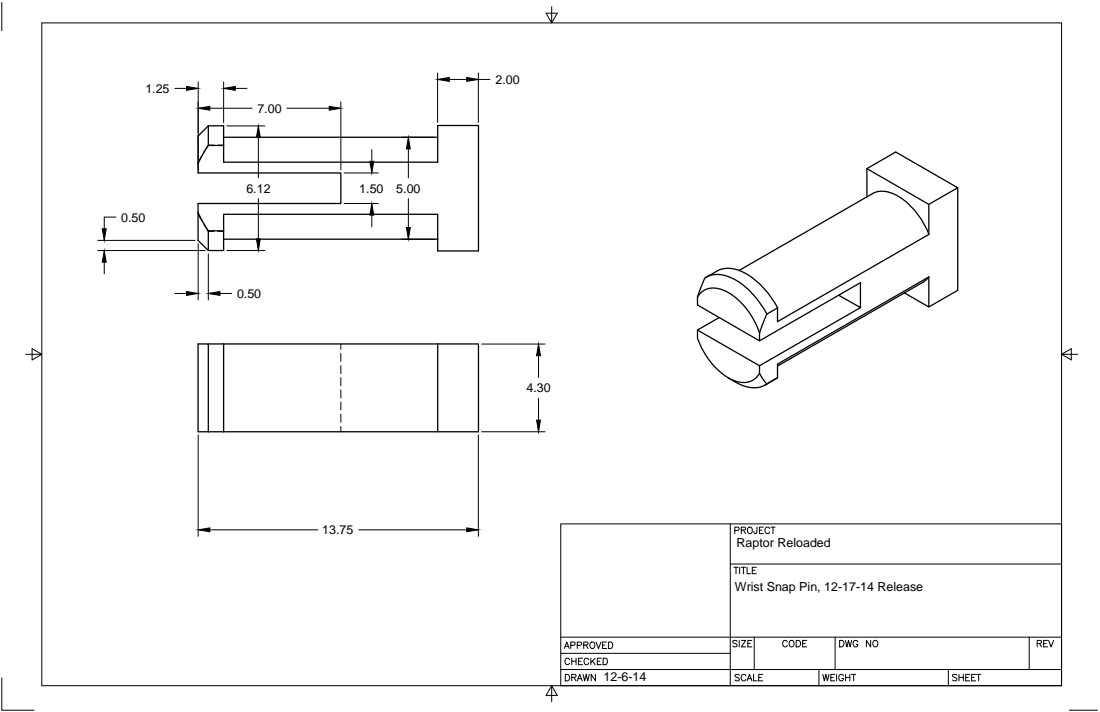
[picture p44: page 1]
Raptor Reloaded

Wrist Snap Pin, 12-17-14 Release

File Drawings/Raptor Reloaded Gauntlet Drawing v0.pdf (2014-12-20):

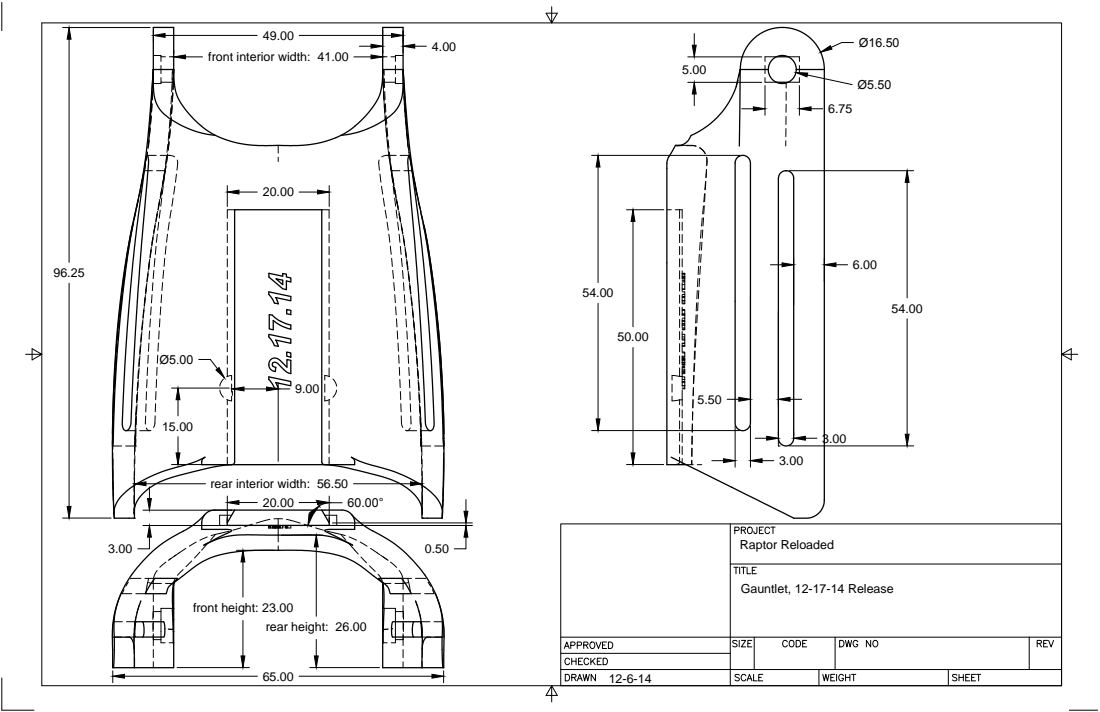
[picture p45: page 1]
front height: 23.00; rear height: 26.00; Raptor Reloaded; Gauntlet, 12-17-14 Release

front interior width: 41.00

rear interior width: 56.50

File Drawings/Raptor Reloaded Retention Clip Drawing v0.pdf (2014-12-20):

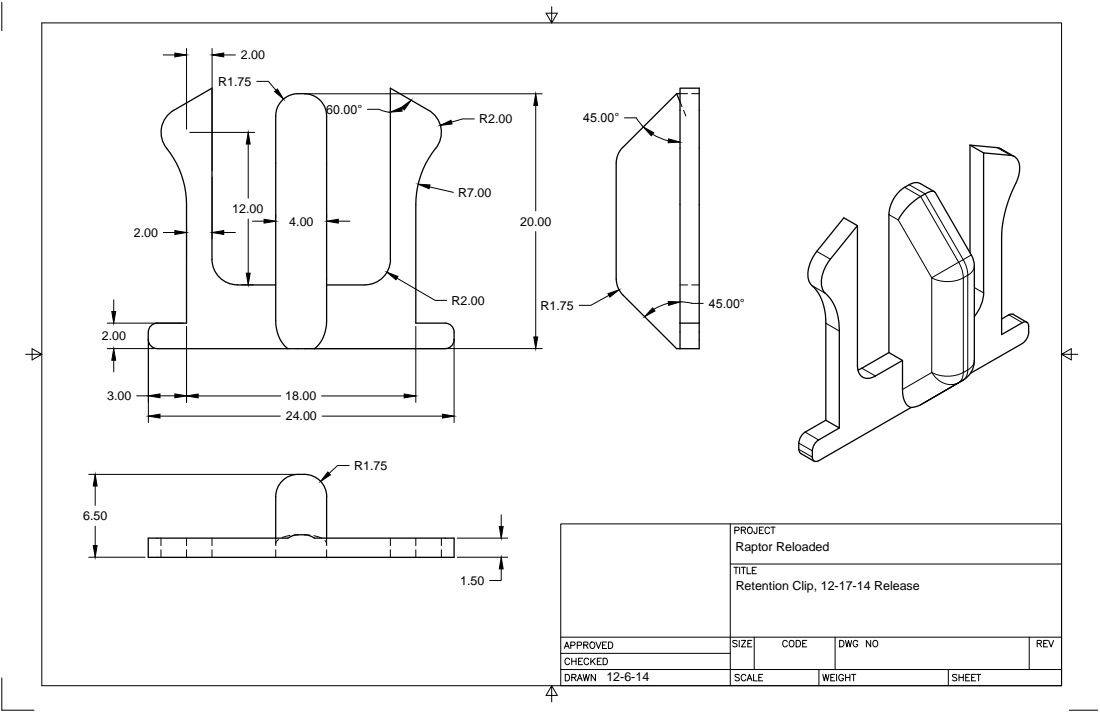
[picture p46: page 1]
Raptor Reloaded

Retention Clip, 12-17-14 Release

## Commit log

2014-12-20 Initial commit of Raptor Reloaded files
    [left palm.stp, raptor_2.0_finger_pin.stl, raptor_2.0_fingertip.stl, raptor_2.0_proximal.stl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]
2014-12-21 added STEP, IGES, F3D source files
    [left palm.stp, raptor_2.0_fingertip.stl]
2015-01-04 updated finger snap pin and full print plates
    [raptor_2.0_finger_pin.stl]
2015-01-04 updated zip with finger pin changes
2015-01-26 added assembly PDF
2015-02-02 Added fingertip with nail
    [raptor_reloaded_fingertip_with_nail.stl]
